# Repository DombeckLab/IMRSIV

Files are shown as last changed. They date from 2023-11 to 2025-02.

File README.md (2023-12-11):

# Overview
This repository contains [Assembly Instructions](https://github.com/DombeckLab/IMRSIV#assembly-instructions), [3D models](https://github.com/DombeckLab/IMRSIV/tree/main/STL), [Zemax models](https://github.com/DombeckLab/IMRSIV/tree/main/Zemax), and Unity environment [files](https://github.com/DombeckLab/IMRSIV/tree/main/Unity_project) and builds ([high quality](https://github.com/DombeckLab/IMRSIV/tree/main/Ultra_Quality_Demos)/[medium quality](https://github.com/DombeckLab/IMRSIV/tree/main/Medium_Quality_Demos)) related to the iMRSIV system, wchih is fully described in [Pinke et al - Neuron 2023](https://doi.org/10.1016/j.neuron.2023.11.019).

As we continue to work on improvements to the system, we are looking for early adopters and any suggestions. Reach out to the study authors if you are interested in using iMRSIV!

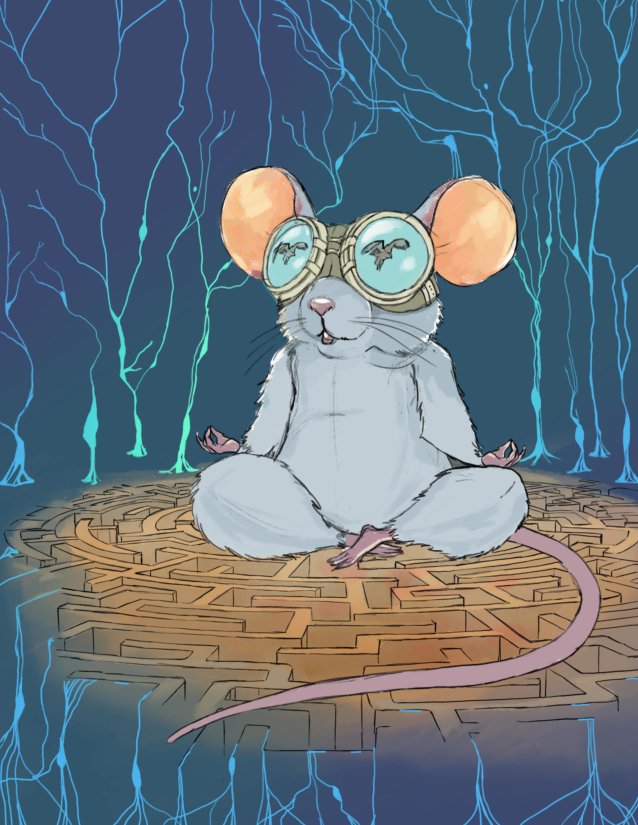
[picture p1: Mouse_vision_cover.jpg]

(Illustration by @Rita)

# Assembly Instructions
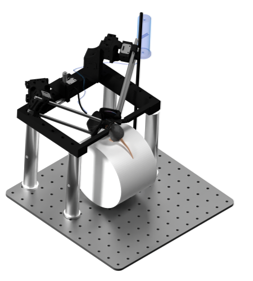
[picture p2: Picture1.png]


## 3D printed parts
[3D models](https://github.com/DombeckLab/IMRSIV/tree/main/STL)
- U-Mount.stl
- Left_Wing.stl
- Left_Lens_Holder.stl
- Right_Wing.stl
- Right_Lens_Holder.stl
- headplate_iMRSIV.stl

## Zemax Files 
[Zemax models](https://github.com/DombeckLab/IMRSIV/tree/main/Zemax)
- MouseEye_Lens.zmx
- MouseEye_Monitor.zmx

## Thorlabs Parts 

- Thorlabs rotation stages: RP005 (2x)
- Post holders: CP02B - 30 mm Cage Mounting Bracket (2x)
- Mini cage posts: MS3R (4x)
- Pillar posts for U-mount (RS4P8E), (4x)
- Thorlabs 3-axis stage: 2x3X MS1S / ARM
- Thorlabs 90 degree angle bracket AB90E 
- Thorlabs imperial, breadboard 1/4-20 tapped holes on 1" centers (1x)

 ## Electronic Parts  
- Displays: 1.4 inch Innolux display (2x), with HDMI controllers (2x) (From Aliexpress 2x KITS)
- Lens: Shanghai Optics, d=12mm, R1=60deg, R2=10deg, CT=4 mm (company contact and stl file) + Zemax files, lens and eye  (2x)
  
 ## Misc
- Norland Optical Adhesive NOA 81, 1 oz.
- Quick glue
- Double component epoxy glue
- 4-40 screw kit
- 3-32 screw kit
- 1/4 screw kit

## Left and Right Wing assembly

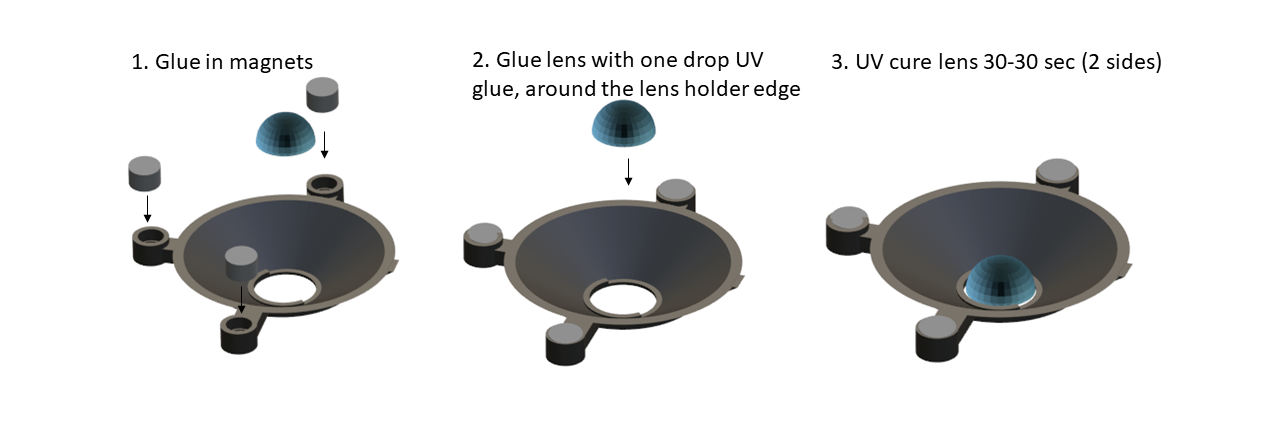
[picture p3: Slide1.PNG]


Print Left_wing.stl. Recommended material is Tough PLA. (Classic PLA is still good) with Z resolution 0.1 mm at least. Finish 3D printing with a fine file or sandpaper, especially the lens holder contact.
1. Glue the 3 magnets into the magnet holes, with Quick glue
2. Set the lens holder on a flat surface (ie. a glass sheet), Put the lens into the holders ring. Apply Norland UV glue and
3. Cure both sides with 60 sec of UV light (300 mw/mm2)

 Repeat steps with Right_wing.stl

## Left and Right display holder glueing

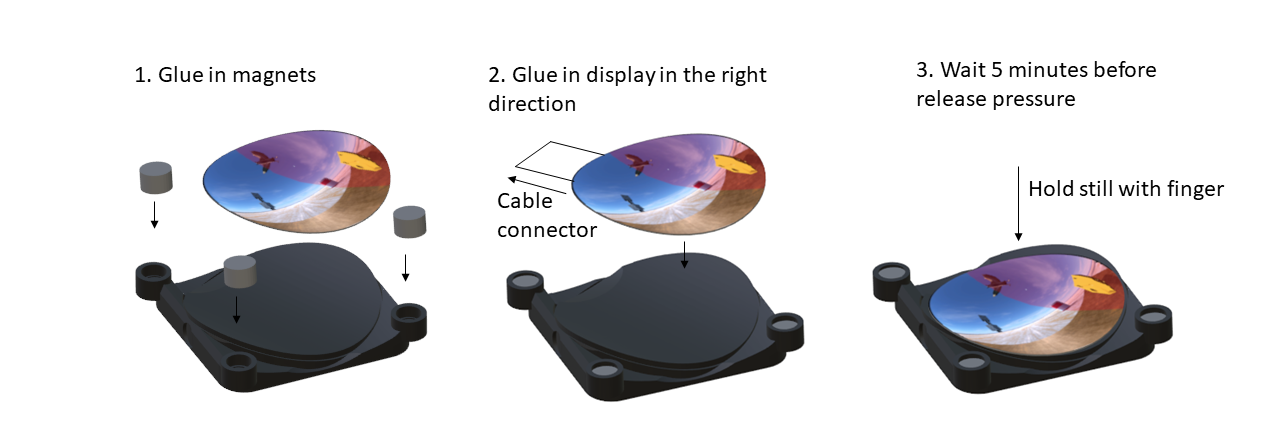
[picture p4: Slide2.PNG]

Print Left and Right wing.stl and finish the edges with fine file
1. Glue in the 3 magnets
2. Apply double component epoxy glue on surface, and carefully adjust the display to the final position. (Connector orientation marked on figure)
3. Hold at least 5 minutes with your finger in bended position, wait another 5 minutes. 

## Arm assembly

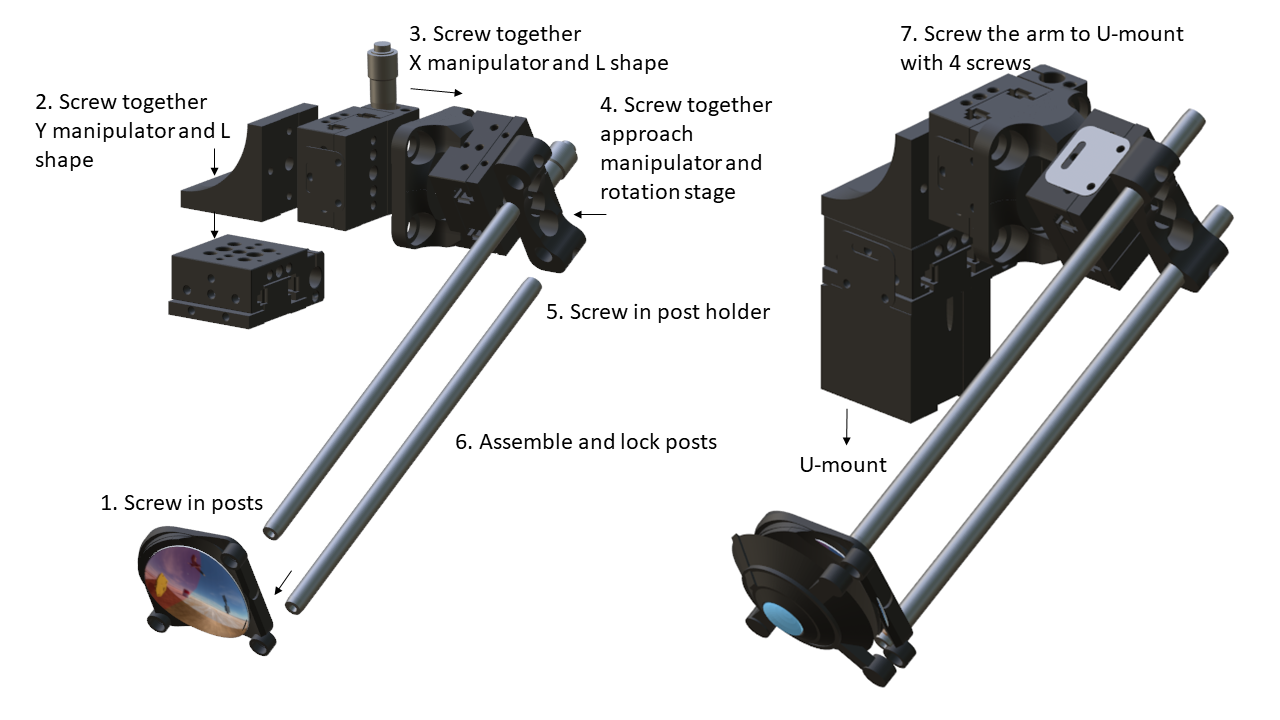
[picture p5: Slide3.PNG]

1. Screw posts into the display holder
2. Scew together Y manipulator and L-shape
3. Screw together X manipulator (and arm) and (Thorlabs angle bracket)
4. Screw together approach manipulator and rotation stage
5. Screw post holder onto rotation stage
6. Assemble and lock posts in postholder
7. Screw the whole arm onto the U-mount with 4 screws

## Setup assembly

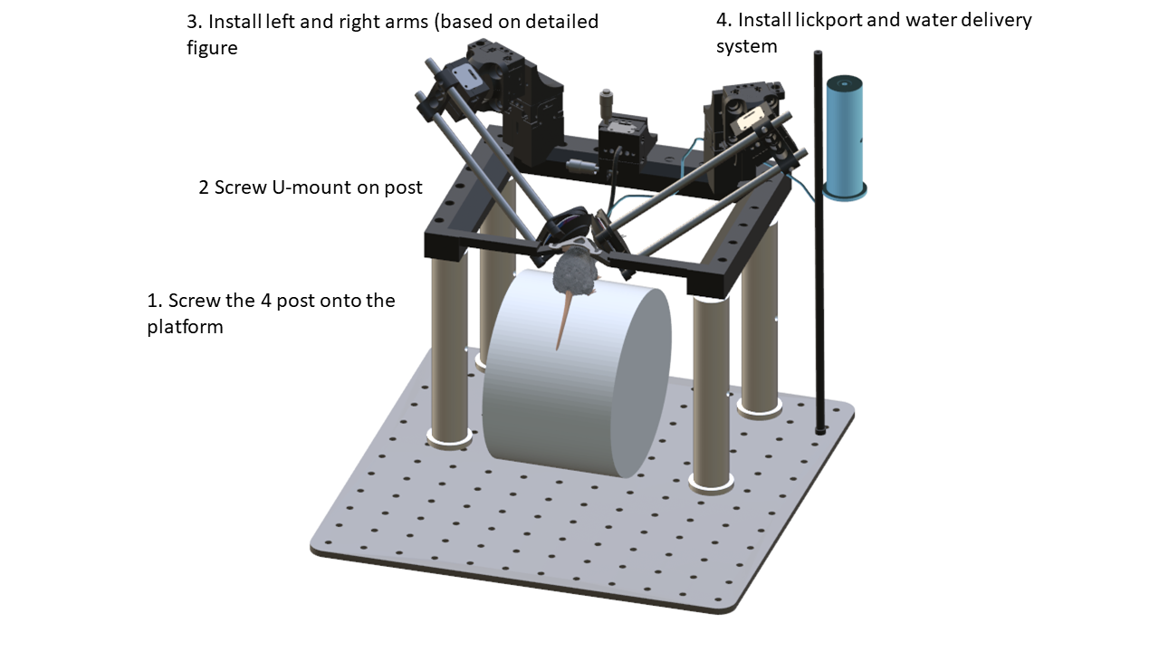
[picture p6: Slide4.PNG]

1. Screw the 4 pillar posts onto the platrform
2. Screw U-mount on post
3. Install and screw on the 2 arms
4. Install any desired components for behavior by mounting to the breadboard or the U-mount
5. Set up display HDMI controllers onto Thorlabs posts, and securely connect displays after assembly

### Final assembled version running Unity

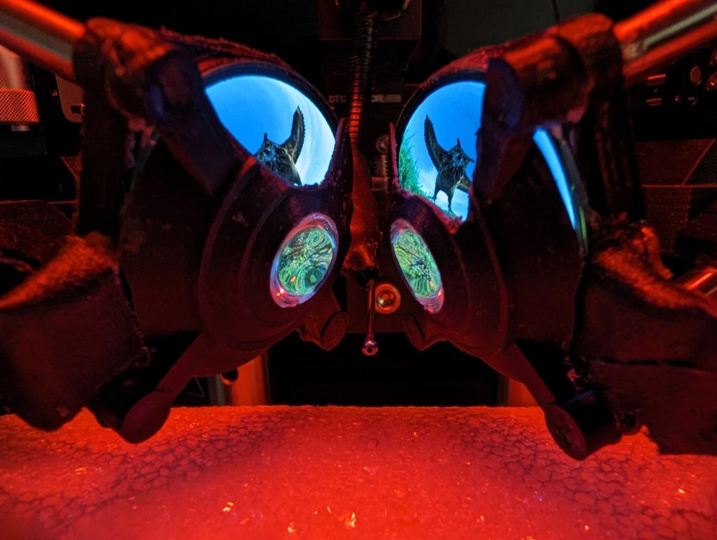
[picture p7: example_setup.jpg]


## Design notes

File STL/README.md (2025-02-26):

# 3D models of custom parts used

## Lens Holder
Piece used to hold lens. Attaches with magnets to Wing. [Left](Left_Lens_Holder.stl) [Right](Right_Lens_Holder.stl)

## Wing
Piece used to hold display. [Left](Left_Wing.stl) [Right](Right_Wing.3mf)

## Target
Piece that can replace Lens Holder and be used for positioning assembly. [Left](TargetLeft.stl) [Right](TargetRight.stl)

## U Mount
Large mount that allows for attachment of all individual pieces. [U Mount](U_mount.stl)

## Headplate
Custom titanium headplate used to attach to the U Mount. [headplate](headplate_iMRSIV.stl)

For alignment during surgery, headplate with targets to align to the eyes. [headplate target](SurgTarg4.stl)

## Lens
3D model of 12 mm [lens](12mmFinal_HQ.stl) along with related [Zemax files](12mm_CAD_ZEMAX).

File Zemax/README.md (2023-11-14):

# Zemax

These are Zemax OpticStudio models of the lens, eye, and monitor used.

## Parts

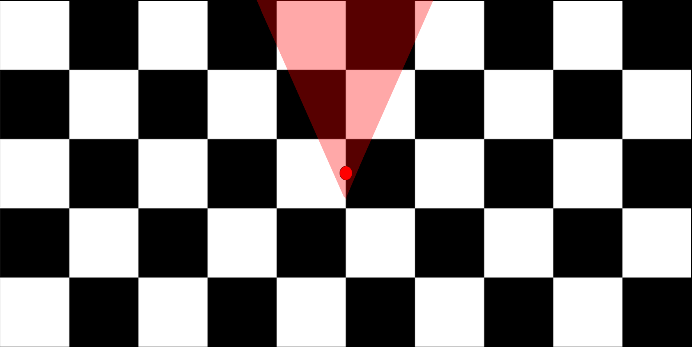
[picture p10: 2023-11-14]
Unity_project/Assets/Wispy Sky/Materials/binocu.png

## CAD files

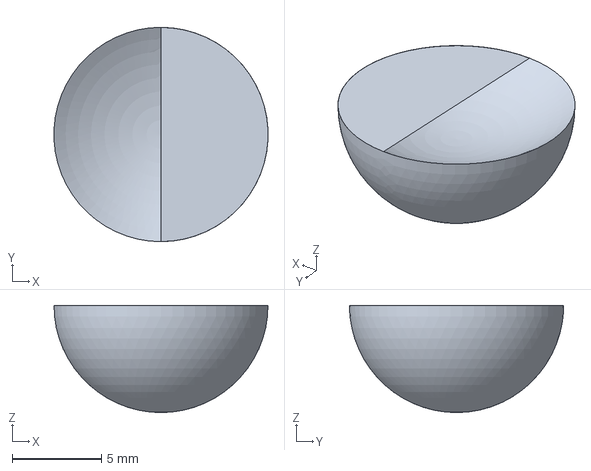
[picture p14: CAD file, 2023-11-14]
STL/12mm_CAD_ZEMAX/12mmFinal.stp
12.0 x 12.0 x 6.00 mm

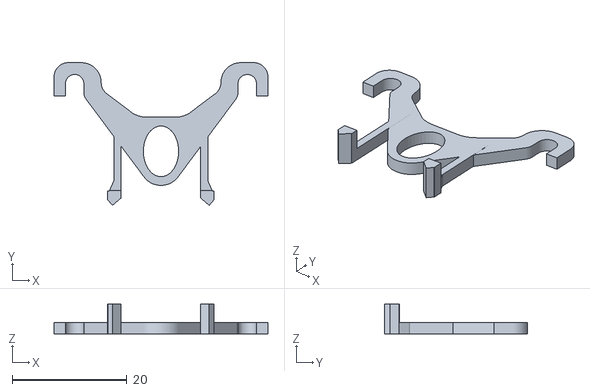
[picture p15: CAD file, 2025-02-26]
STL/SurgTarg4.stl
37.3 x 24.9 x 5.22

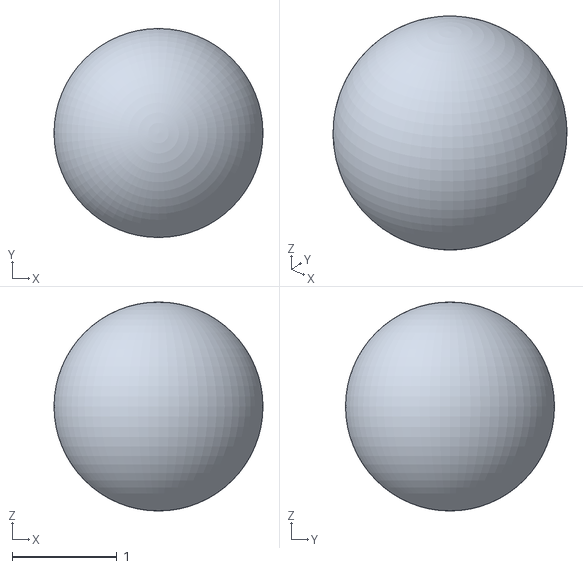
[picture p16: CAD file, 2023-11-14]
Unity_project/Assets/Fisheye/Graphics/Prefabs/sphere64.obj
2.00 x 2.00 x 2.00

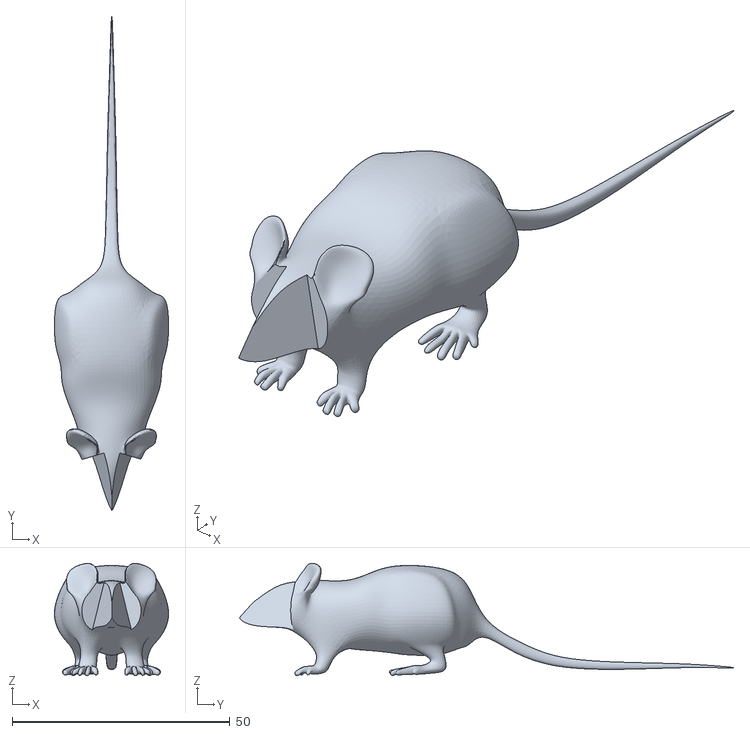
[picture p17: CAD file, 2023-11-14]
Unity_project/Assets/Prefabs/mouseCamera_ver1.obj
26.2 x 113.5 x 25.8

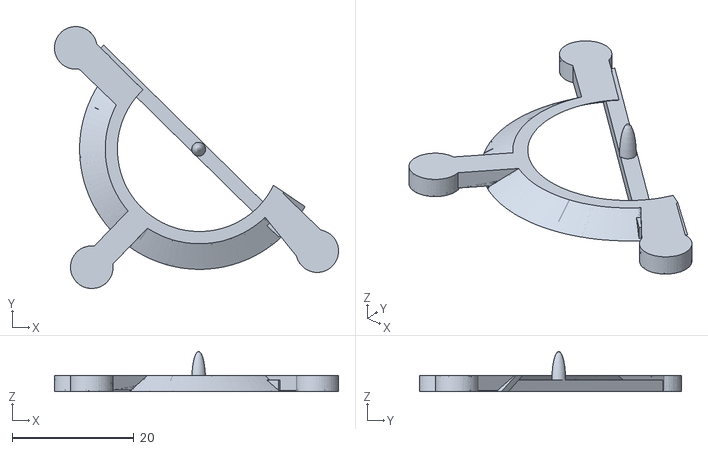
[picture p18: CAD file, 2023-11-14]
STL/TargetLeft.stl
46.6 x 42.9 x 6.60

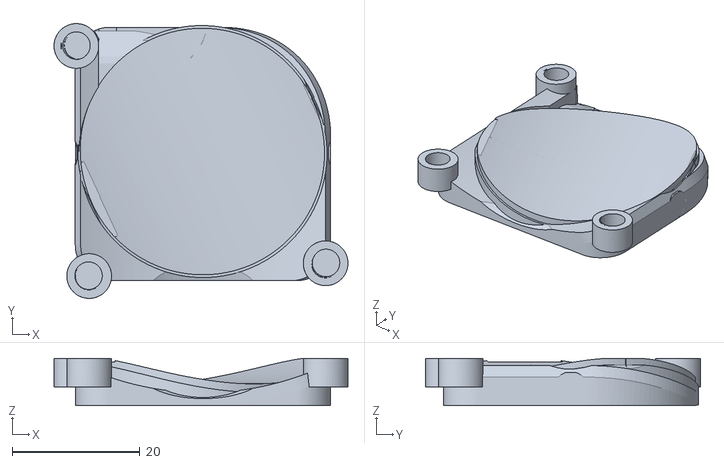
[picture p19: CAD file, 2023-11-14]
STL/Left_Wing.stl
46.0 x 43.0 x 7.35

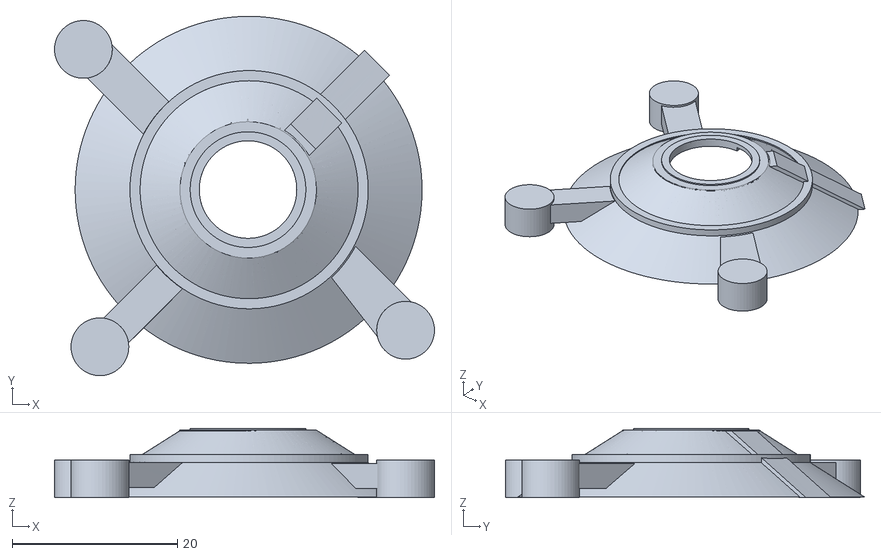
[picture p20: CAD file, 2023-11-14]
STL/Left_Lens_Holder.stl
46.0 x 43.5 x 8.37

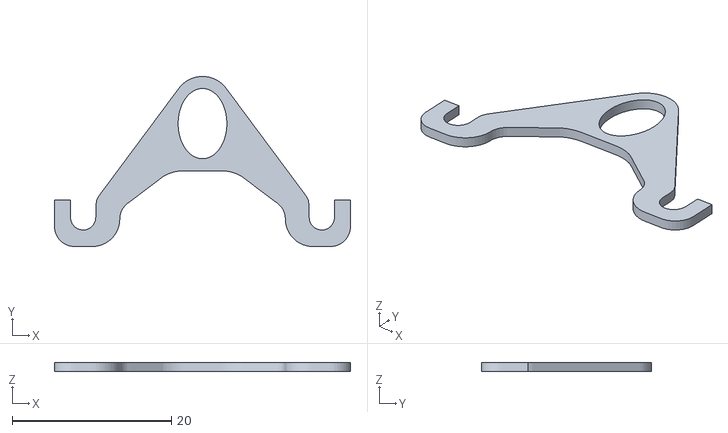
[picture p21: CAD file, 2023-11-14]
STL/headplate_iMRSIV.stl
37.2 x 21.4 x 1.14

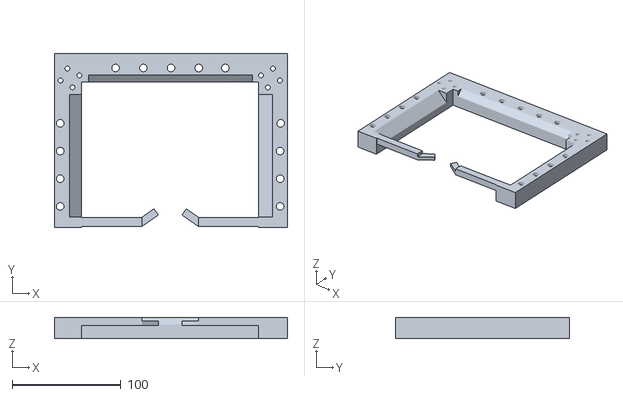
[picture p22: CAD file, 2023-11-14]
STL/U_Mount.stl
213.8 x 159.4 x 19.7

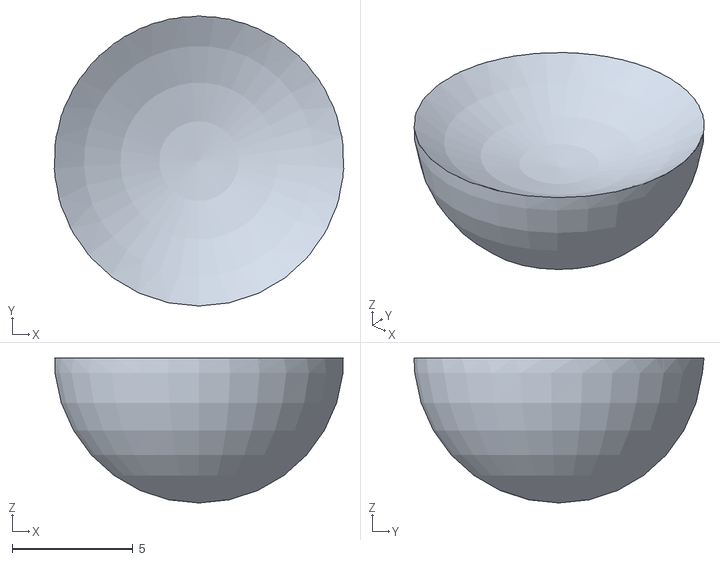
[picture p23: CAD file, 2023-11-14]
STL/12mmFinal_HQ.stl
12.0 x 12.0 x 6.00

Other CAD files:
STL/TargetRight.stl
STL/Right_Wing.3mf
STL/Right_Lens_Holder.stl
